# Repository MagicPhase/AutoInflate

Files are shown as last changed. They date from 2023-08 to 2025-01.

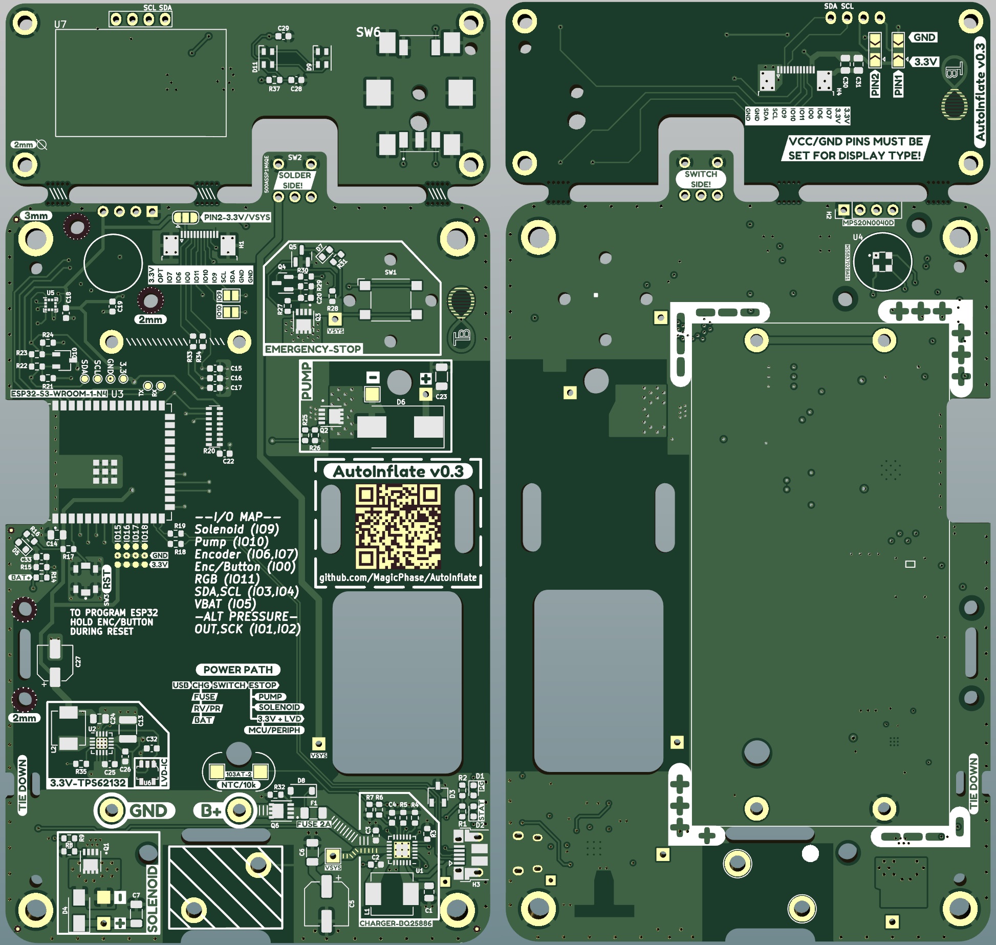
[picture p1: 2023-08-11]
PCB/AutoInflate_V0.3_PCB.jpg

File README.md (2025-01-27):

# AutoInflate
Custom-designed solution for inflation-style sensory and anxiety vests. 

**_In memory of Pedro Martin Colea @tahunus 1/24/24. His initial interest and motivation to create a refined version of my old prototype made this project possible. I'm grateful for the opportunity to have stepped outside my comfort zone and bring this project to fruition. Thank you, Pedro._** 

<br>

###

Welcome! This page contains all the necessary files and instructions to build this device. Please read through each section carefully! If you've found this page, you're seeking to build your own automated inflation device based on this design for inflation-style sensory and anxiety vests. My goal for designing this device was to automate the inflation and deflation cycles on my own [Squease Vest®](https://www.squeasewear.com/). My thanks to [@tahunus ](https://github.com/tahunus) for giving me the inspiration to continue the development of this project!

**_Update 11/28/23: It appears that Squease will be relaunching soon! This is good news for those unable to get a vest prior to the company shutting down operations earlier this year. Yay!_**

It was my intention to design this with a wide range of possible uses while also making it relatively safe given minimal instruction to the user. Here's an overview of some features.
* Handheld/Pocket Sized
* Encoder Style Input
* Emergency Stop Button
* Configurable Pressure Limits
* Adjustable Timed Cycles
* Tap To Activate (coming soon)
* Wireless Function (coming soon)

While this device was created using the Squease Vest, this device could possibly be used with any other inflation-style garment. How this is accomplished will be determined by the end user who will also be responsible for any and all modifications required to mate with this device. 

### ⚠ A note about safety! Under proper working conditions using sanely determined pressure limits and times, this device can operate safely but also has the potential to restrict breathing! This is true for adults, _but especially true for small children._ If you're unsure about how to safely assemble and operate this device, you should consider using the supplied method of inflation for your garment. To make this as safe as possible, I've implemented an E-Stop button on the front side that is a kill switch that removes power from the functional parts. Both the E-Stop and main power switch will effectively render the device unable to retain pressure using the "normally open" air solenoid.

### ⚠ Important note: While the AutoInflate does have safety features like reverse protection and is fused, the charger IC (U1) BQ25886 does not have a 2-cell balance function! This means you should take extra care when choosing and installing the 18650 batteries. Ensure they are both of the same make and model battery. You should also try to match their respective internal resistance to ensure they discharge and recharge evenly, but most importantly to ensure they are at the same level of charge when you install them! If you are unsure about their level of charge, place both cells in an external charger and charge them both together before installation. Once you have two "matched" and charged 18650 batteries then you can safely install them. They will discharge and recharge at the same rate and ensure safe operation by the charger IC.

### It's also important to note that the 18650 holders internally are sized for "flat top" cells and not "button top". The button top cells are too long and will not fit! Please check you're using the correct size 18650 flat-top cells. 

<br>

[STEP 1 - VEST](https://github.com/MagicPhase/AutoInflate#step-1---vest)<br>
[STEP 2 - PLAN](https://github.com/MagicPhase/AutoInflate#step-2---plan)<br>
[STEP 3 - ASSEMBLE](https://github.com/MagicPhase/AutoInflate#step-3---assemble)<br>
* [STEP 3.1 - Main PCB](https://github.com/MagicPhase/AutoInflate#step-31---main-pcb)<br>
* [STEP 3.2 - Display PCB](https://github.com/MagicPhase/AutoInflate#step-32---display-pcb)<br>
* [STEP 3.3 - First Power-Up](https://github.com/MagicPhase/AutoInflate#step-33---first-power-up)<br>
* [STEP 3.4 - Final Assembly](https://github.com/MagicPhase/AutoInflate#step-34---final-assembly)<br>

[STEP 4 - SOFTWARE](https://github.com/MagicPhase/AutoInflate#step-4---software)<br>
* [STEP 4.1 - UI Description](https://github.com/MagicPhase/AutoInflate#step-41---ui-description)<br>
* [STEP 4.2 - Code Explanation](https://github.com/MagicPhase/AutoInflate#step-42---code-explanation)<br>
* [STEP 4.3 - Modify The Menus](https://github.com/MagicPhase/AutoInflate#step-43---modify-the-menus)<br>

## Please read through these hardware sections before considering a BOM.

[3D Printed Parts](https://github.com/MagicPhase/AutoInflate/blob/main/Materials.md#-3d-printed-parts-)<br>
[Pressure Sensor Manifold Options](https://github.com/MagicPhase/AutoInflate/blob/main/Materials.md#-pressure-sensor-manifold-options-)<br>
[Fasterns and Metal Parts](https://github.com/MagicPhase/AutoInflate/blob/main/Materials.md#-fasterns-and-metal-parts-)<br>
[PCB](https://github.com/MagicPhase/AutoInflate/blob/main/Materials.md#pcb)<br>
[Electrical Components](https://github.com/MagicPhase/AutoInflate/blob/main/Materials.md#electrical-components)<br>
[Non-Electrical Components](https://github.com/MagicPhase/AutoInflate/blob/main/Materials.md#non-electrical-components)<br>

[0.3v FIRMWARE](https://github.com/MagicPhase/AutoInflate/blob/main/FIRMWARE/AUTOINFLATE_0.3.1V.ino)<br>

# _**STEP 1 - Vest**_

It's advisable that you gain access or purchase the desired inflation garment first. This will be an important step to understanding the operation of the garment and the possible benefits of using an automated inflation device for such a garment. At the time of this writing, the Squease Vest® has been out of production for most of 2023. However, recent news says they might be starting up again! 

# _**STEP 2 - Plan**_

<br>

Determine what hardware is needed. You'll need to acquire the parts needed to craft your AutoInflate so go over these sections and start building your purchase list. As of this writing, building a single AutoInflate could cost between $200-300 depending on the availability and quantity of parts you buy. One significant cost will be the manufacturing of the unassembled PCB. 

Example: $16 x 5 minimum + shipping to US = $100. [PCBWAY](https://www.pcbway.com/).

* [3D Printed Parts](https://github.com/MagicPhase/AutoInflate/blob/main/Materials.md#-3d-printed-parts-) Go over the necessary 3D printable parts you'll need. You can use a print service such as [Shapeways](https://www.shapeways.com/) or any other printing service that's capable of reproducing the needed resin parts. I've included some helpful notes beside the parts to guide you in your decision-making. DIY printing is an option, of course, however, the enclosure may be tricky to print if you don't have experience with large flat surfaces. I'd recommend a print service for this unless you feel comfortable doing this part. I had many failures until I figured out my printer!<br>

* [Pressure Sensor Manifold Options](https://github.com/MagicPhase/AutoInflate/blob/main/Materials.md#-pressure-sensor-manifold-options-) Determine which pressure mainfoild you wish to use. I recommend using the parts listed for [MS583702BA01](https://www.digikey.com/en/products/detail/te-connectivity-measurement-specialties/MS583702BA01-50/6221400). I've not fully tested the MPS sensor variant! This is important because the two pressure sensor variations require different resin prints as well as sensor hardware. The MS583702BA01 sensor has the benefit of having a higher pressure limit but is also slightly more expensive. _Note: there are I2C pads exposed so a completely different sensor could be used if the internal space allows for it!_
* [Fasterns and Metal Parts](https://github.com/MagicPhase/AutoInflate/blob/main/Materials.md#-fasterns-and-metal-parts-) Make a list of the various fasteners and metal parts needed.
* [Electrical Components](https://github.com/MagicPhase/AutoInflate/blob/main/Materials.md#electrical-components) Make a list of the various electrical parts needed.
* [Non-Electrical Components](https://github.com/MagicPhase/AutoInflate/blob/main/Materials.md#non-electrical-components) And also make a list of the non-electrical parts needed.

And finally, the PCB.
* [PCB](https://github.com/MagicPhase/AutoInflate/blob/main/Materials.md#pcb) I've provided the appropriate Gerber files for a PCB manufacturing service. Both the main and display PCBs are together and separated during assembly. If you plan to DIY, I'd recommend ordering the solder stencil as well!
* Follow the [BOM](https://github.com/MagicPhase/AutoInflate/blob/main/PCB/AutoInflate_V0.3_BOM.html) and build the appropriate list of SMD components. (Save to BOM.html and open in any browser.)

# _**STEP 3 - Assemble**_

Once you have all the parts and pieces, you can move to assembly and testing! 

## _**STEP 3.1 - Main PCB**_

These instructions assume you have moderate to advanced skills necessary to solder the surface mount parts. You can use the included interactive [BOM](https://github.com/MagicPhase/AutoInflate/blob/main/PCB/AutoInflate_V0.3_BOM.html) to guide you as you build the PCB. 

* Please refer to [Materials](https://github.com/MagicPhase/AutoInflate/blob/main/Materials.md) section as you progress!<br>

* The top side of the main PCB should be soldered first. All the surface mount parts are located on one side with one exception being the MS5837 pressure sensor which should be done after soldering all the top side SMD parts. A hot plate can be used for the top side soldering while  **_the back side pressure sensor MS5837 requires a hot air station to attach!_** The alternative MPS sensor requires through-hole soldering. It's important to attach the sensor prior to the completion of the PCB assembly due to its proximity to the battery holder. It's possible to reflow this after, but you'd need to cover or remove the battery holder so as to not damage it from the heat! Ensure all the parts are soldered correctly and remove any solder jumps between pins. **This is especially important for the USB and display ribbon connectors!** 

||||
| :--: | :--: | :--: |

* Attach and solder the remaining components like the battery holder, pump (including shock mount), and solenoid. Also, check that the motor polarity is correct! Depending on the specific model of the solenoid, it may also have a polarity. If the solenoid shows no polarity, connect whichever way is convenient to the pads. Both pump and solenoid wires run from the backside to the front through holes in the PCB.
* The shock mount foam piece should be thin open cell foam about 7cm x 2cm in size and no more than 5mm thick un-compressed. This is important so as to not overfill the cavity surrounding the pump motor. <br>

||| |||
| -- | -- | -- | -- | -- |

* Prepare and attach the MS5873 sensor manifold. Don't forget the O-Ring! Refer to the exposed example of the assembly. Once done you can mark and cut the lengths of silicon tubing to connect the various parts. The larger is 1/8"(3mm) ID x 15mm in length and the smaller is 3/32"(2mm) ID x 9mm in length.<br>

|||
| -- | -- |

* The finished main assembly should now look something like this. Note there is a small slot marked "Tie Down" on the PCB for a single zip tie to attach. Don't over-tighten or you'll cut off the airlines. This is meant simply to contain the tubing. Also, remember that ALL the through-hole parts are on the back side! Make sure the power switch is correctly mounted before attempting to fit into the case! <br>

||||
| -- | -- | -- |

* Before moving on, this is a good time to glue the two light pipes in place as well as the 5 threaded metal inserts. Using CA glue, glue the indicator LED light pipe into the TOP case as well as the E-Stop light pipe. During testing, the E-Stop light pipe is more optional because the LED tends to light up the entire E-Stop button. However, it's important to glue the TOP indicator before assembling further. Also using either CA glue or epoxy, glue the 5 inserts into their respective notches in the BOTTOM case halve.

|||
| -- | -- |

## _**STEP 3.2 - Display PCB**_

The next step is to solder and assemble the display PCB. This is done in two parts.
1. Solder the SMD parts using air hot like capacitors, resistors, ribbon cable socket, and encoder.
2. **The last step is to attach the OLED, but it first needs to be fitted into the casing.**

* Please refer to [Materials](https://github.com/MagicPhase/AutoInflate/blob/main/Materials.md) section as you progress!<br>

* The display board has components on both sides and may be tricky to solder. Because the encoder is a surface mount part, I'd recommend attaching that first because it requires a little extra heat. Once you have the display board soldered MINUS the OLED, connect the solder jumpers on the back side to match your OLED pin configuration. Specifically which pin is power and ground. This should be silk-screened on the device and you should jumper the correct pins to match.<br> <br>

* Start by laying out the TOP case, OLED, and the display PCB. Set the OLED into the case, then arrange the PCB to fit with the screw holes visible. Make sure the pins from the OLED header pass through the appropriate holes. Screw the PCB in place with the M2 self-tapping screws. Make sure everything is secured and finally solder the 4 header pins. This will set the proper distance between the OLED and PCB. Note that the OLED is held in place by the pin header and the allowed seat internal to the case. You can now remove the PCB assembly by pivoting backward at the bottom. This will make it easier to attach the ribbon cable if you don't feel comfortable doing it inside the case.

|| | | |
| -- | -- | -- | -- |

## _**STEP 3.3 - First Power-Up**_

All the components should be assembled for the first power-on test. On the bench, install the 18650 batteries and attach the ribbon cable between the two boards. Note that the device can't be used directly from USB power! The battery charger requires the batteries to be installed to work properly!

* Please refer to [Materials](https://github.com/MagicPhase/AutoInflate/blob/main/Materials.md) section as you progress!<br>

* ## ⚠Important note: While the AutoInflate does have safety features like reverse protection and is fused, the charger IC (U1) BQ25886 does not have a 2-cell balance function! This means you should take extra care when choosing and installing the 18650 batteries. Ensure they are both of the same make and model battery. You should also try to match their respective internal resistance to ensure they discharge and recharge evenly, but most importantly to ensure they are at the same level of charge when you install them! If you are unsure about their level of charge, place both cells in an external charger and charge them both together before installation. Once you have two "matched" and charged 18650 batteries then you can safely install them. They will discharge and recharge at the same rate and ensure safe operation by the charger IC.

* On the first power-on using a bench supply, you should see the green LED next to the ESP32 light up when the voltage reaches 5.8v if you've followed the schematic and used the specified IC for (U6). U6 is the low-cutoff IC and will cut power to the 3.3v supply when a low threshold of 5.8v is reached. Without any programs running, the OLED should remain blank at this point. Install the 2 x 18650s and connect the micro USB to ensure the charger is working. You should see both the STAT and PG LEDs light up. Both of these LEDs are connected to USB 5v and the "Open Drain" pins on the charger IC (U1). The STAT LED will stop once the batteries are fully charged. If no LED activity is visible on the charger, ensure the batteries are installed in the correct orientation and double-check the USB header for solder blobs!<br>

* Check the E-Stop is working correctly. This is important to ensure the safe use of this device. While powered, press the E-Stop button. This will activate the E-Stop circuit and cut power to both the ESP32, solenoid, and pump indicated by the red LED. If this circuit fails to cut power or doesn't function as intended, please review the SMD components and ensure they match the schematic. This trip circuit will remain active until the device is powered off.<br>

https://github.com/MagicPhase/AutoInflate/assets/104283546/334833f4-76d6-4969-865c-a28765c14681

## _**STEP 3.4 - Final Assembly**_

Finally, it's time to assemble the finished unit. It's easier to disconnect the ribbon cable from the main PCB and reattach it just prior to combining the two case halves. The 1/8" thru-bulk fitting should be attached to the bottom case as well as a final short piece of tubing that should be used to connect the sensor manifold to the thru-bulk port. 

* Please refer to [Materials](https://github.com/MagicPhase/AutoInflate/blob/main/Materials.md) section as you progress!<br>

* The thru-bulk fitting should be placed with the nut on the outside. This allows for a bit more room on the inside for the short tube. The main PCB assembly should fit snuggly inside the case bottom. The short tubing piece and be cut to fit once the PCB has been seated. Make sure the PCB fits onto the two indexing pins that are molded into the case model.<br>

|| 
| -- | -- |

* Lay both halves flat on a table and attach the ribbon cable. Each of the sockets has a bottom carriage that needs to be pulled out slightly before inserting the ribbon cable. The cable should be inserted all the way with the shiny metal pins facing up then evenly push the carriage into place. This is easy to mess up and have the cable seat slightly crooked. This needs to be perfectly straight to work correctly.

|| | |
| -- | -- | -- |

* Place the E-Stop button into the guide holes in the PCB. While keeping the BOTTOM case on the table, rotate the TOP half over and allow the ribbon cable to fold over itself. The two halves come together by inserting the single TOP screw mount into the BOTTOM case at an angle. Then pivoting down over the E-Stop button and aligning the remaining screw holes. It's important to remember the forwardmost screw mounts make a near-zero clearance between the PCB and TOP case. Because of this, it's necessary to slightly force the TOP case as it pivots onto the BOTTOM case. As the two halves come together, it's necessary to gently guide the E-Stop button into place under the casing to not be crushed or cause assembly issues. I've included a video showing how to disassemble and reassemble the device at this point. Watch this first! ---> https://www.youtube.com/watch?v=enySG7zAhLk<br>

|| 
| -- | -- |

* Once done, use the remaining 5 screws 4 x (M3-0.5 x 12mm) and 1 x (M3-0.5 x 8mm) to secure the case.


## _**STEP 4 - SOFTWARE**_

Uploading the firmware is done using the [Arduino](https://www.arduino.cc/en/software) IDE or other compatible software to compile and upload the code to the ESP32.

The latest firmware can be found here. --> [FIRMWARE](https://github.com/MagicPhase/AutoInflate/tree/main/FIRMWARE)

A note about programming the ESP32-S3 using the onboard USB to UART.

To program the ESP32 you need to hold down the encoder button and then power on. This shorts PIN 0 to ground putting it into program mode. Then plug in the USB and check for a COM port.

For some reason, the Arduino IDE picks a random hardware ID for the ESP32. It will probably show up as some flavor of S3, which it is, but the compiler profile needs to know that it's an "ESP32S3 Dev Module"! It will probably still compile and upload, but the random ESP32-S3 module profile usually doesn't have the correct settings or correct IO mapping. The latter issue caused me great headaches when I was programming for the first time. This also means when resetting after a flash, the device ID changes and you need to reselect it if you're monitoring for serial connection. All my ESP32s act this way on the newer Arduino IDE so I assume it's not an isolated problem.<br>



Also, if you plan to use serial debug back over the USB, make sure you have the "USB CDC" option enabled on your first flash otherwise no traffic.<br>



## _**STEP 4.1 - UI Description**_

A description of the various menu items.

**_Important note: All entered settings will be valid for the current powered cycle. If you wish the settings to remain during future uses, use the SAVE function on each specific subconfig menu!_**

### Main Page



* Current Pressure - Displays the current pressure of the system in PSI (pound per square inch).

* STOP - This function will stop all current cycles and turn off the pump and solenoid.

* HUG - This function is intended for a one-time inflation cycle. These settings can be changed and saved in the CONFIG menu.

* PROFILE - This function is for multiple cycles within a total cycle duration time. These settings can be changed and saved in the CONFIG menu.

* CONFIG - This accesses the main subconfigure selection menu.

* ACTIVITY - This will animate whenever a cycle is running regardless if there's any current activity from the pump.

* TIME REMAINING - This counter shows the current remaining time until the active cycle stops.

* BATTERY - Shows the remaining battery life. The low mark is referenced to the low voltage cutoff IC voltage (U6).

### Config Page



* A simple menu for the selection of the various subconfiguration menus. At the time of this writing, not all menus are active.

### Hug and Profile



Both the Hug and Profile menus are similar. The Hug settings are intended for one-time inflation cycles while the Profile is meant for multiple cycles based on a total cycle time.<br>

**_Important note: Neither the Hug or Profile cycles will run if the On Time and Cycle Time are zero!_**

* Target Pressure - The desired target pressure to maintain during an on cycle.

* On Time - The amount of time to maintain the target pressure before reverting to a zero pressure state within the cycle time.

* Off Time - The amount of time for the system to remain at zero pressure before re-inflating within the cycle time.

* Cycle Time - The hard time limit for multiple inflation cycles. This time limit will allow for multiple on/off times within this limit, but will not be divided evenly. 
  * Example 1: On Time = 40 seconds, Off Time = 20 seconds, Cycle Time = 5 minutes (5:00). There will be a total of 5 on/off cycles within the 5 minutes.
  * Example 2: On Time = 30 seconds, Off Time = 60 seconds, Cycle Time = 9 minutes and 20 seconds (9:20). There will be a total of 6 on/off cycles with a remaining 20 seconds of on time before the cycle limit is reached and stops the run.

* BACK - Use to navigate back to the subconfig selection menu.

* HELP - An on-screen description of the various items.

* SAVE - This function will save the current entered pressures and times within for future use if powered off.

### AIRSYS



This page is important for proper function! Please adjust these settings based on personal therapeutic choices such as maximum allowed pressures and pump speeds.

* Pump Max - This sets the maximum speed of the pump. For the maximum performance, the highest setting should be used. However, if the audible pump noise is an issue, you can reduce this speed to quiet the pump motor at the expense of a slower inflation time. Consideration should be given because the slower speed may fail to reach a target pressure within a given On Time cycle.
  * Example: If the device is unable to inflate the vest's volume of air at a given "On Time", try increasing the pump speed or increase the On Time to achieve the target pressure within the On Time cycle.
 
* P.Max - This sets the maximum allowed target pressure in both the Hug and Profile menus. (Note: The limit of this adjustment is hard coded.)

* THRESH - This adjusts the threshold limit for the ramping function. This allows for a slow ramping of the pump motor at the top and bottom of the target pressure making for a quieter start and stop. Change to 0 if you don't want this function.

* BACK - Use to navigate back to the subconfig selection menu.

* HELP - An on-screen description of the various items.

* SAVE - This function will save the current entered pressures and times within for future use if powered off.

## _**STEP 4.2 - Code Explanation**_

This section is to provide a brief description of the menu system in code. This may be helpful if you wish to add or modify the menus.

It's important to remember this menu system is based on a one-button interface with the encoder and that all stored and displayed values are derived from the ENCODER INPUT VALUE! This was a design choice based on my limited knowledge of coding in general and my need to keep things relatively easy to adjust with only the encoder as an input device. This meant jumping through some hoops to achieve this. For example, all pressures and stored and computed as (millibar * 100), but the displayed and adjustable values are all in 0.1 PSI increments for ease of use. This means the stored value in (millibar * 100) is computed bidirectionally from the displayed PSI in 0.1 increments from the encoder input and also recalled from memory as (millibar * 0.0146) both computed and displayed as a whole number which is the encoder input value. This gives around 6.8 millibar resolution which is more than enough for this application. Furthermore, variables like the pump PWM are also derived from the encoder input but are further divided by the number of pixels in the graphic representing the pump speed. In this case, the pump speed is mapped to the number of pixels on the display graph which gives 51 levels of adjustment. This mapping can be removed with the pump PWM reflecting the exact encoder input, but the resolution is 10 bit giving 1024 levels. 10 bit was chosen for greater control over low PWM values in the 'airSYSLOOP()' function.

The code keeps track of the current page and element number based on the encoder value and whether the button was pressed on a specific element. The "main" and "sub-config" selection pages have specific/special action functions that are different from the individual sub-config pages which are more generalized. 

Displayed data on the various pages is handled with the 'displayData()' function in 'void loop()' which loads the data to display based on the current page number and results in a continuous page update of that data. Each specific page function contains the relevant data to display such as graphics and variables as well as things like cursor positions and specific variable constrain limits. 

Both the encoder and button are handled with interrupt functions. While the button function is an interrupt, it's also debounced and checked on each loop. A button action happens using a combination of page number, element, and encoder value. This happens when the page number is passed to 'buttonPressFunc(pageNumber)' and is a one-time action that changes the continuously displayed data.

Here are a few flowcharts that describe how data is displayed. Remember both the first two pages, Main and Sub-Config Selection pages have different action functions than the more generalized sub-config pages themselves. Also, it's important to remember these charts are generalized and don't contain the total of executed functions during a button press but can be a useful guide for the order of execution! 

## Main and Config Page Blocks



## Sub-Config Pages (PROFILE, HUG, etc...)



The specific sub-config page elements are selected and changed in real-time based on the element number and whether 'changeValue' is true or not.

## _**STEP 4.3 - Modify The Menus**_

Here's an example of changing and adding elements to the last config page which is currently empty (0.3v). This is the last config page 'configPage8()' (which needs to be added), and the 10th page in the system 'pageNumber = 10'. We will change the onscreen title from "----------" to "TEMP". We will then add a new onscreen variable "TEMP" with a selectable range from 0-255 and include the 'Preferences' entry to store the variable in flash. Also included will be the default onscreen back and save buttons. This will result in 3 total elements for 'configPage8()'. (0, Back) (1, TEMP) (2, SAVE) "Back" and "Save" functions are special cases and handled by the 'subconfigPageActions()' function during a button press. The zeroth element goes back to the sub-config selection menu by default and only needs the onscreen graphical elements in each specific sub-config page. The Save function can be at any element number except zero and also only needs the onscreen graphical elements in each specific sub-config page. See the template below 'configPage8()' for an example of the Save function on element number 2. All other onscreen elements will need specific graphics, text, variable handling, encoder limits, etc...<br>



Nearly all the graphics for this project were generated using [lopaka.app](https://lopaka.app/) U8g2 code generator. This webapp has greatly reduced the time for generating the graphical elements so check it out!



* First, change the displayed title of the 8th config page from "----------" to "TEMP" in the following section of 'void configMainPage()'.<br>

```
else if(encoderInput == 8)//PAGE 8 NA
  {
    u8g2.setDrawColor(1);
    u8g2.setFont(u8g2_font_profont22_tr);
    //u8g2.drawStr(11, 32, "---------"); //<--From this.
    u8g2.drawStr(39, 32, "TEMP");        //<--To this.

    if(!flash)
    {
      u8g2.setDrawColor(1);
      u8g2.drawFrame(89, 54, 10, 10);
    }
    else
    {
      u8g2.drawBox(101, 54, 10, 10);
    }
  }
```

* Second, add a 10th case to the 'displayData()' function below case 7. This will be the looping display data for the 8th config page 'configPage8()' which is 'pageNumber = 10'.<br>

```
void displayData()//CONTINUOUS EXECUTE
{
  switch (pageNumber)
  {
    case 1:
      mainPage(); //MAIN PAGE
      break;
    case 2:
      configMainPage(); //CONFIG PAGE
      break;
    case 3:
      configPage1(); //PROFILE
      break;
    case 4:
      configPage2(); //HUG
      break;
    case 5:
      configPage3(); //AIRSYS
      break;
    case 6:
      configPage4(); //MOTION
      break;
    case 7:
      configPage5(); //CONFIG
      break;
    case 10:
      configPage8(); //<---NEW TEMP PAGE!!
      break;
    default:
      break;
  }
}
```

* Third, add a function 'void configPage8()' with the relevant data.<br>

```
void configPage8()//TEMP
{
  if(SAVE){SAVE = false;} //Important! Because the save function is picked up in the button handle portion instead of on each sub-config menu, this function forces the execution when the encoder input is equal to the element number for the save function only!

  //Initial page graphics.

  u8g2.setDrawColor(1);
  u8g2.drawXBMP( 0, 57, 9, 7, image_Pin_arrow_left_9x7_bits);        //Back button.
  u8g2.drawXBMP( 104, 53, 24, 11, image_KeySaveSelected_24x11_bits); //SAVE button.
  u8g2.setFont(u8g2_font_profont22_tr);
  u8g2.drawStr(19, 35, "TEMP");

  //Using the 'u8g2.drawStr()' may require the use of 'dtostrf()' to disaply data.
  char buf[5];
  int temp = tempVar;
  dtostrf(temp, 3, 0, buf);
  
  u8g2.setFont(u8g2_font_profont22_tr);
  u8g2.drawStr(72, 35, buf);

  //Alter the displayed data or variables based on encoder input and element.
  
  if(!changeValue) //Check if we're changing a selected value.
    {
      if(encoderInput == 0)//BACK
      {
        if(!flash)
          {
            u8g2.setDrawColor(0);
            u8g2.drawBox(0, 57, 9, 7);
          }  
      }
      else if(encoderInput == 1)//New Temp Variable
      {
        encoderInputTemp = tempVar;
        if(!flash)
        {
          u8g2.setDrawColor(1);
          u8g2.drawFrame(70, 19, 38, 18);
        }     
      }
      else if(encoderInput == 2)//SAVE
      {
        if(!flash)
          {
            u8g2.setDrawColor(2);
            u8g2.drawRBox(104, 53, 24, 11, 1);
          }
          SAVE = true;//Set SAVE flag for button press trigger when the save icon is highlighted. (Special case)
      }
    }
    else //Now if changeValue is true, we are making changes to the specific element that was selected. Element == 0 goes back to the sub-config selection menu by default!
    {
      if(element == 1)//TEMP VARIABLE
      {
        encoderConstrainValMin = 0; 
        encoderConstrainValMax = 255;  //It's important to set a maximum encoder input value!
        tempVar = encoderInput;        //Live update to variable.
      }
      else if(element == 2)//SAVE
      {
         //LEAVE BLANK. The save function is checked by setting 'SAVE = true' above and picked up in the 'subconfigPageActions()' function.
      }
    }
}
```

* Fourth, add the temp global variable near the top of the code.<br>

```
byte tempVar = 0;
```

* Fifth, add the number of elements of the new temp page to constrain the encoder behavior. We are adding only two elements to this page so we change the 11th position of 'PageElements[11]' from 0 to 2. The zeroth element is a back function by default in the sub-config menus. The page order is as follows: BLANK, MainPage, ConfigPage, Profile, Hug, AirSYS, Motion, Config, WIFI, -----, (NEW TEMP PAGE).<br>

```
int PageElements[11] = {0, 3, 8, 6, 4, 5, 0, 3, 0, 0, 2};
```

* Sixth, add the correct 'Preferences' entry to the 'storedData()' function to store in flash. In the 'storedData()' function, change the case 10 (page number 10) execution to this...<br>

```
case 10:
 if(!RW) //READ
 {
  tempVar = preferences.getUInt("temp_Var", 0); //Check if tempVar is present, if not set default value '0'.
 }
 else //WRITE
 {
  preferences.putUInt("temp_Var", tempVar); //Write tempVar to flash at 'temp_Var' namespace in Preferences ESP32 storage function.
 }
 break;
```

* Seventh, add a function to pull stored value from flash on power up in 'void setup()'.<br>

```
storedData(10, 0); //Page number 10, '0' for read.
```

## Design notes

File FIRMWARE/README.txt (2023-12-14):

AUTOINFLATE V0.3.1 - 11/18/23
BY Tevian Busselle 

This version (0.3.1v) only has the MS5837 pressure sensor enabled, and will not work with the MPS sensor yet. This also requires the MS5837 library found here. https://github.com/bluerobotics/BlueRobotics_MS5837_Library Copyright (c) 2015 BlueRobotics

This ino file must be compiled and uploaded using the Arduino IDE with all relevant ESP32 libraries.

What works:
All basic functions like timed inflation cycles work. This includes a one-time cycle "HUG" and a repeating timed cycle "PROFILE". 
The ability to configure basic settings such as pressure settings, pump speeds, and times. Each menu also has a save function for continuing use after power cycles. 

What's doesn't work:
The tap to activate with the onboard IMU has not been coded for yet. This also includes any WIFI/Bluetooth options. Both of these menus are empty at the moment.

Important interface notes:
* Inputting pressures over the selected maximum will reduce the value to the maximum. 
* An inflation task "hug or profile" will only execute if the times are not zero!
* The values under all menus except CONFIG are usable for the current power cycle. The SAVE function will store the values for future use. 
* Changing the CONFIG menu items requires a reset to take effect. This is forced in the CONFIG navigation.

Operation notes:
* The pump's noise level can be tuned by changing the maximum PWM in the AIRSYS menu. The threshold ramping value can also be adjusted to allow for a softer start/stop
  that can make the pump quieter during the initial start and topping maintenance.
* Motor pulses for system feedback. (One) pulse for system functions such as the save function or failure to set a variable. (Two) pulses single the end of an inflation task.
* the threshold ramping pressure works by ramping the pump speed from a low minimum to a high speed across a small pressure window at the beginning and end of an inflation cycle.
  This means the pump speed will remain low until the pressure sensor sees an increase in pressure. Depending on the volume of air required to inflate the vest or vessel,
  this can result in an extended duration of low pump output at the beginning of the inflation cycle. If this happens, try decreasing the threshold amount, increasing the pump speed,
  ensuring the total volume of air in the vest or vessel is reduced (adjusting the fit), or setting the threshold number to 0 which disables this feature.
  
---------------------------------------
Choosing the correct pressure is important! Correct pressure is a matter of personal choice 
based on your therapeutic needs. While I can't give a specific pressure and time duration, 
I can give a few useful guides. Don't forget to 'SAVE' the settings if you find something you like for future use!

Example Hug setting: 
This will provide a rather quick and sudden sense of pressure on the torso for 30 seconds or more if needed. 
Adjust the pressure as needed!

  Hug Menu
    Pressure: 1.0-1.5
    Time: 0:30-1:00
  CONFIG Menu
    Pump PWM: 100%
    T.MAX: 0.0-0.2  

Example Profile setting: 
These settings will give a gentle continuous rise and fall of pressure. 
This can be very relaxing or decompress from anxiety or stress.

  Profile Menu
    Pressure: 1.0
    On-Time: 0:45-1:00
    Off-Time: 1:00-2:00
    Cycle Time: 10:00-15:00
  CONFIG Menu
    Pump PWM: 60-75% (This will make the pump quieter) 
    T.MAX: 0.3-0.4 (This will result in a softer start/stop)

Notes about the code:

All variables including pressures, settings, and times are converted from the (encoderInput) counter. This has the effect of limiting the divisions of certain
variables like pressure and pump speeds. For instance, while the pump PWM has a value from 0-1023, this would require the encoder to be turned too many times
to achieve the maximum value. The division of the PWM speed is dictated by the number of pixels in the display graph. This is handled via the map function to
convert 0-1023 steps into 51 pixel steps. The raw PWM number is stored for use while the displayed value/graph is converted from that stored number. 

While the displayed pressures are in PSI, the stored pressure values are in (mBar * 100). Example: The default stored value for the maximum "selectable" 
pressure from the interface is (13788 / 100 = 2PSI) and is stored in (airSys.maxPressure). 

When uploading the firmware it's important to remember there is a hard-coded maximum system pressure. In the code, this variable sets the maximum encoder input 
value allowed when adjusting the maximum pressure in the AIRSYS menu. This variable is called (MaxPressure). 
Example: MaxPressure = 41 is 4.1PSI (encoderInput / 10). If the "selectable" pressure is also 4.1PSI then the stored value in (airSys.maxPressure) would be 27576. 

When the selectable pressure is reduced, all stored pressures in the different run scenarios are also reduced to match this. So, while the P.MAX adjustment in the 
AIRSYS menu sets the maximum user-selectable pressure for the different run scenarios, the hard-coded variable (MaxPressure) sets that maximum value for the adjustable 
P.MAX value in the interface.

Default system variables like pressures and PWM are stored in "storedData" function with the relevant variables. The preference function initiates these defaults.

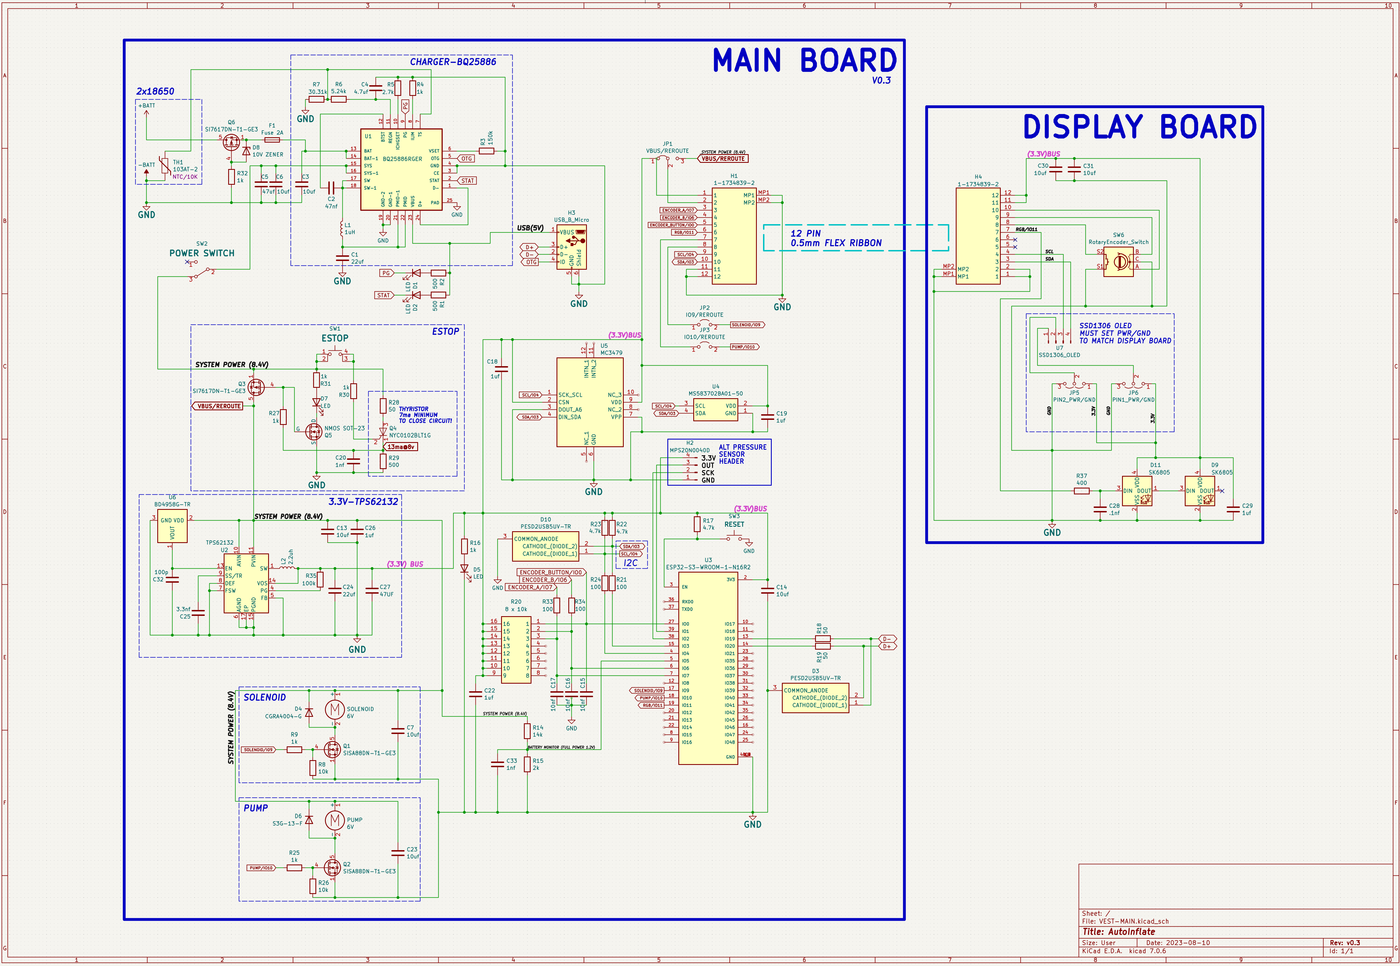
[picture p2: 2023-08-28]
PCB/AutoInflate_V0.3_Shematic.png

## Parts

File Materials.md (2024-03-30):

# Enclosure Hardware

## -3D Printed Parts-

This section outlines the necessary 3D-printed pieces to make and assemble a completed unit. Before printing these parts at home or purchasing from a printing service it's important to note that some parts require specific resin types to ensure proper function.

| Part             | 3D model       | Description/Note  |
| :---             | :---:          | :---             |
| **Top Enclosure**    | TOP_small | Due to the complexity it's recommended this part be made of resin vs filament. To ensure this part is impact-resistant I recommend [Siraya Tech Fast ABS-Like](https://siraya.tech/products/fast-abs-like) or equivalent. Other resins can be used, but beware of the brittleness and impact resistance of the resin. [OBJ](https://github.com/MagicPhase/AutoInflate/blob/main/3D%20FILES/OBJ/TOP.obj), [STL](https://github.com/MagicPhase/AutoInflate/blob/main/3D%20FILES/STL/TOP.stl)|
| **Bottom Enclosure**| BOTTOM_Small | This piece is less complex than the top and could possibly be printed in PLA, PETG, or TPU filament. Print orientation may be critical however to ensure the PCB mounting points and index pins are correctly positioned and flat. For the best results, I recommend this part also be resin printed in [Siraya Tech Fast ABS-Like](https://siraya.tech/products/fast-abs-like) or equivalent impact-resistant resin. [OBJ](https://github.com/MagicPhase/AutoInflate/blob/main/3D%20FILES/OBJ/BOTTOM.obj), [STL](https://github.com/MagicPhase/AutoInflate/blob/main/3D%20FILES/STL/BOTTOM.stl)|
| **Pump Shock Mount** | MOTOR_MOUNT_Small | Shock mount for the pump motor. This piece is ***optional*** to dampen the pump noise during operation, but it's highly recommended! While it's possible to simply zip-tie the pump to the PCB with some foam padding, during operation, this can transfer a large amount of noise and vibration to the unit. There is an option to reduce pump output to limit the noise level, but this shock mount reduced the overall noise by more than half. The walls of the band are <0.8mm for reference. It's possible to have this part filament-printed with PETG or TPU on the vertical axis, but it's also recommended to have this resin printed with [Siraya Tech Fast ABS-Like](https://siraya.tech/products/fast-abs-like), [Siraya Tech Tenacious -Flexible](https://siraya.tech/products/tenacious-resin-flexible-resin), or equivalent flexible resin. This part can be delicate to handle due to the thinnest part being <0.8mm. [OBJ](https://github.com/MagicPhase/AutoInflate/blob/main/3D%20FILES/OBJ/MOTOR%20MOUNT.obj), [STL](https://github.com/MagicPhase/AutoInflate/blob/main/3D%20FILES/STL/MOTOR%20MOUNT.stl)|
| **EStop Button** | ESTOP_Small | This is the EStop button that rests on the EStop switch on the PCB. It protrudes through the PCB with 4 guide pins. These pins are <2mm in diamater. This part could possibly be filament printed, ***however***, due to filament prints having ridges, this might make the guide pins rub and stick to the PCB and interfere with the button press. Because of this, it's recommended this part be printed in a non-brittle red-colored resin. [OBJ](https://github.com/MagicPhase/AutoInflate/blob/main/3D%20FILES/OBJ/BUTTON.obj), [STL](https://github.com/MagicPhase/AutoInflate/blob/main/3D%20FILES/STL/BUTTON.stl)|
| **EStop Light Pipe** *Optional*| EStop_Light_Pipe_Small | This light pipe is an optional part that transfers the red EStop light from the PCB to the top of the enclosure. During testing, however, the light also illuminates the EStop button itself and may not be required. Because of its size, this needs to be resin printed in any clear or white resin. [OBJ](https://github.com/MagicPhase/AutoInflate/blob/main/3D%20FILES/OBJ/ESTOP%20LightPipe.obj), [STL](https://github.com/MagicPhase/AutoInflate/blob/main/3D%20FILES/STL/ESTOP%20LightPipe.stl)|
| **Indicator Light Pipe** | INDICATOR_LIGHT_PIPE_Small | This part is cosmetic and transfers the light from the two RGB LEDs on the top part of the enclosure. This can be printed in resin and possibly filament in either clear or white. [OBJ](https://github.com/MagicPhase/AutoInflate/blob/main/3D%20FILES/OBJ/LIGHT%20PIPE.obj), [STL](https://github.com/MagicPhase/AutoInflate/blob/main/3D%20FILES/STL/LIGHT%20PIPE.stl)|

<br>
<br>

## -Pressure Sensor Manifold Options-

One of the two options ***must*** be decided before finishing a BOM list.

| Part             | 3D model       | Unit Example | Description/Note  |
| :---             | :---:          | :---:        | :---              |
|*Option 1*| ---------- | ---------- | ---------- |
| **Manifold Cap** |MANIFOLD_V0 4_Small|MANIFOLD_V0 4_ASSEMBLE_Small|This manifold is required for the [MS583702BA01](https://www.digikey.com/en/products/detail/te-connectivity-measurement-specialties/MS583702BA01-50/6221400) sensor. It's intended to cover the SMD sensor itself and sealed to the PCB with an O-Ring and M2 screws and nuts. It connects the pump, solenoid, and port, and requires a quality resin print to ensure an air-tight seal around the O-Ring and PCB. I recommend [Siraya Tech Fast ABS-Like](https://siraya.tech/products/fast-abs-like) or equivalent. Current version is V0.5. [OBJ](https://github.com/MagicPhase/AutoInflate/blob/main/3D%20FILES/OBJ/Air%20Manifold%20V0.5.obj), [STL](https://github.com/MagicPhase/AutoInflate/blob/main/3D%20FILES/STL/Air%20Manifold%20V0.5.stl)|
| M2-0.4 x 12mm (2) | M2-0 4 12mm | | Two 12mm screws. |
| M2 nut (2)        | M2 nut | | Two M2 nuts.|
| O-ring (1)  | O-Ring | | One O-ring to seal against the PCB. This part needs to be 9mm(OD) x 5mm(ID) x 2mm. Note that 4.8mm(ID) O-rings will also work.|
|*Option 2*| ---------- | ---------- | ---------- |
| **Manifold 4-Way** | MANIFOLD_4_WAY_Small | MANIFOLD_4_WAY_ASSEMBLE_Small | This manifold is required for the MPS20N0040D/HX710B pressure sensor assembly. This is a cheaper alternative and can be found on Amazon for a few dollars. This manifold is a 4-way that connects the pump, solenoid, sensor, and port and requires a quality resin print is ensure an air-tight seal around the ports. I recommened [Siraya Tech Fast ABS-Like](https://siraya.tech/products/fast-abs-like) or equivalent.  It is secured with M2 screws. Current version is V0.2. [OBJ](https://github.com/MagicPhase/AutoInflate/blob/main/3D%20FILES/OBJ/Air%20Manifold%20V0.2.obj), [STL](https://github.com/MagicPhase/AutoInflate/blob/main/3D%20FILES/STL/Air%20Manifold%20V0.2.stl) |
| M2-0.4 x 4mm (2) | M2-0 4 4mm | | Two screws are needed to secure the manifold to the PCB.|

<br>
<br>

## -Fasterns and Metal Parts-
List of fasting hardware required for the enclosure and manifold options.

| Part             | PICTURE       | Unit Example  |Description/Note   |
| :---             | :---:          | :---:        | :---              |
| M3-0.5 x 8mm (1)   | M3-0 5 8mm |M3_SCREW | One 8mm screw is required on the back side of the enclosure. |
| M3-0.5 x 12mm (4) | M3-0 5 12mm |M3_SCREW_1 | Four 12mm screws are required on the front side of the enclosure. |
| M2 x 6mm (4) Self-tapping | M2x6 | Display Back | Mounting screws for display PCB.|
| M2 x 6mm (4) Self-tapping | M2x6 |MOTOR_MOUNT_Example | Mounting screws for the motor mount. |
| M2 washers (4) | M2 washer|MOTOR_MOUNT_Example | Washers for the motor mount. |
| M3 x 3 x 5mm (5) Heat Set Inserts | INSERTS | INSERT_example | The bottom enclosure is notched for standard M3 x 3mm thick x 5mm round heat set inserts for 3D printing. The resin doesn't work well with heat inserts so I notched the mounting points so they can be secured with epoxy or SA glue. | 
| 2mm x 22mm (2) Stainless Steal Pins |  pin |pin | Two stainless steel strap pins for the top enclosure. These are optional in case you want to use 15mm straps. The pins should be between 22-25mm in length. [Amazon](https://www.amazon.com/dp/B07M63LPFD?ref=ppx_yo2ov_dt_b_product_details&th=1)|

<br>
<br>

# PCB
Main and Display PCBs. Follow the included link for all current PCB files. [PCB FILES](https://github.com/MagicPhase/AutoInflate/tree/main/PCB)
| Part             | 3D model       | Description/Note  |
| :---             | :---:          | :---             |
| **PCB** | PCB_Small | The provided gerber files contain both the MAIN and DISPLAY PCBs. This PCB is made as one piece and separated during assembly. Current version is V0.3. [PCB FILES](https://github.com/MagicPhase/AutoInflate/tree/main/PCB), [Schematic](https://github.com/MagicPhase/AutoInflate/blob/main/PCB/AutoInflate_V0.3_Shematic.png)|

<br>
<br>

# Electrical Components 
Internal Electrical components.
| Part             | 3D model       | Description/Note  |
| :---             | :---:          | :---             |
| Air Pump|  | Commonly called a "370 Pump" or "Mitsumi R-14 A213" is a 6V rated micro air pump. <br> Picture is from an eBay listing. [eBay](https://www.ebay.com/itm/191898244021) |
| Solenoid Valve Normally Open<br>PND-05A-06 or equivilent |  | Common 5-6V rated N/O solenoid valve. It's very important to use an N/O (Normally Open) valve to ensure safe operation. There are mounting holes on the PCB for a genuine PND-05A-06, but an equivalent can be used with zip-ties. This part should measure approximately 20mm x 15mm x 13mm and have a port with 3-4mm(OD). Sub-miniature 3V valves are NOT suitable! Picture is from an eBay listing. [eBay](https://www.ebay.com/itm/262483459557) Also listed as TDS-V05B 6V.|
| SSD1306 OLED 128 x 64|  | Common 0.96" SSD1306 OLED screen. The Display PCB can be configured for either V/G/SCL/SDA or G/V/SCL/SDA depending on which model you get. Picture from [electronicwings.com](https://www.electronicwings.com/sensors-modules/ssd1306-oled-display). |
| 12pin 0.5mm x 100mm flex ribbon cable | Flex Ribbon | Standard 12pin 0.5mm pitch x 100mm length flex ribbon cable. These are common and can be ordered from Amazon as a "Cable Replacement for PS4" or other controllers. This cable is the link between the main and display PCBs. Picture from [Amazon](https://www.amazon.com/gp/product/B08MVZW6QC/ref=ppx_yo_dt_b_search_asin_title?ie=UTF8&psc=1).|
| 18650 (2) flat-top and<br> 2 cell PCB mount holder|BATTERY|Two standard 18650 flat-top batteries and a 2 cell PCB mount battery holder. Avoid using button top cells! [Amazon](https://www.amazon.com/Battery-Storage-Plastic-Parallel-Projects/dp/B0B1JJZ363/ref=sr_1_3?crid=3AY9UWBKUSLFS&keywords=18650%2B2%2Bcell%2Bholder&qid=1693306644&sprefix=18650%2B2%2Bcell%2Bholde%2Caps%2C145&sr=8-3&th=1) |

<br>
<br>

# Non-Electrical Components 
Internal and external components.
| Part             | 3D model       | Description/Note  |
| :---             | :---:          | :---             |
| Encoder Knob |  Knob | Standard 1/4"(6mm) shaft knob. The knobs I chose are 17mm(d) x 16mm(h) knurled aluminum. The enclosure space allows for approximately 17mm in diameter. These are the specific ones I used. [Amazon](https://www.amazon.com/dp/B07TXYBB7Z?psc=1&ref=ppx_yo2ov_dt_b_product_details) |
|Silicon Tubing| Tubing| *Two different sizes are needed.* For the best fit on the pump and port air lines, use 1/8"(3mm)ID tubing. 1/4"(6mm)OD is recommended but thinner can be used if you take precautions to not kink the lines around corners. For the solenoid valve, a smaller tubing of 2mm(ID) x 4mm(OD) fits best. You should be using two different sizes of tubing and both manifolds are sized to fit this arrangement. Picture from [Amazon](https://www.amazon.com/gp/product/B07V5T31MF/ref=ppx_yo_dt_b_search_asin_title?ie=UTF8&th=1)|
| Low Density Foam | FOAM | Thin low density foam for the motor mount. Any thin compressible foam can be used that's less than 1/16"(1.5mm) when compressed. The noise dampening from the motor shock mount is inversely affected by using too much or too thick of foam. The motor should float in the mount to get the best results. Avoid using high-density foam or neoprene! <br><br> The amount needed is approximately 3/4"(15mm) x 3"(75mm). Picture from [Amazon](https://www.amazon.com/Frost-King-Conditioner-Filters-Open/dp/B000BO68BU/ref=sr_1_3?crid=ZTJQQDA5XK5J&keywords=thin+air+filter+foam&qid=1693389469&sprefix=thin+air+filter+foam%2Caps%2C145&sr=8-3)|
| Thru-Bulk Barbed Fitting | Thru-Bulk | A thru-bulk fitting is used to attach to the outside. The specific size I used was 3/16". I wouldn't use anything bigger as it won't fit the tubing inside. Picture from [Amazon](https://www.amazon.com/gp/product/B08SCDC28R/ref=ppx_yo_dt_b_search_asin_title?ie=UTF8&th=1). |

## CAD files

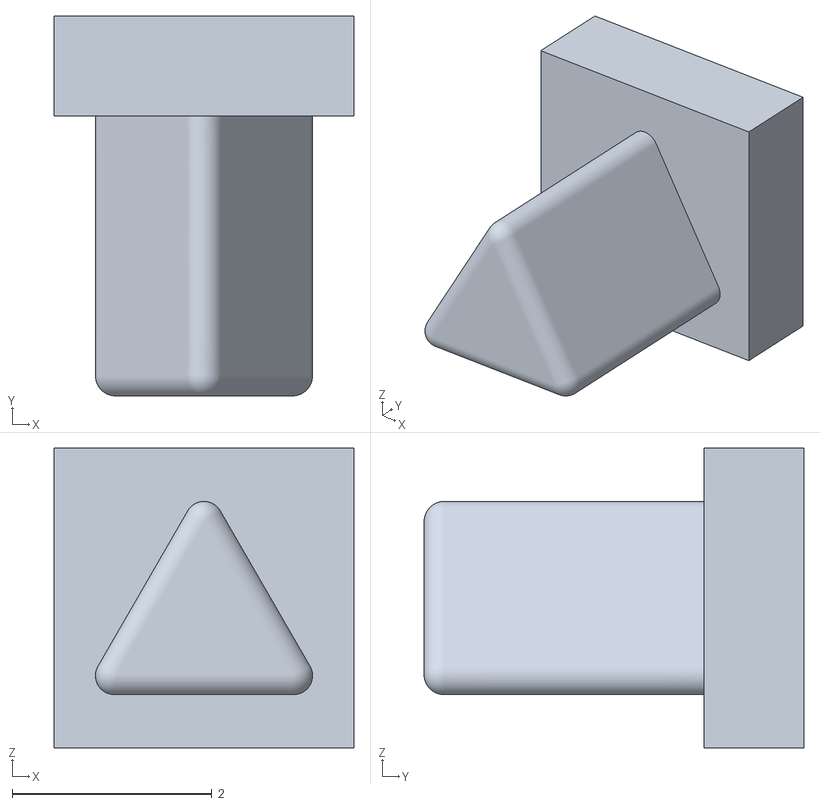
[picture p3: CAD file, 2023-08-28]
3D FILES/STL/ESTOP LightPipe.stl
3.00 x 3.80 x 3.00

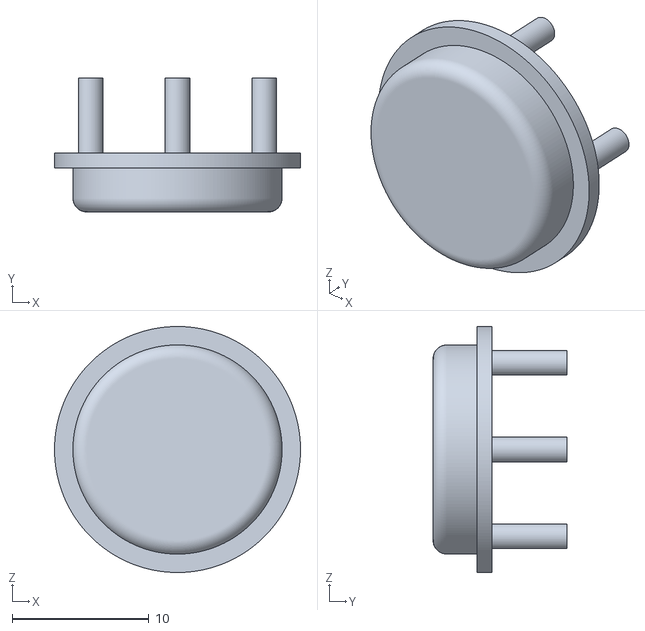
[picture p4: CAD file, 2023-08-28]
3D FILES/STL/BUTTON.stl
18.0 x 9.80 x 18.0

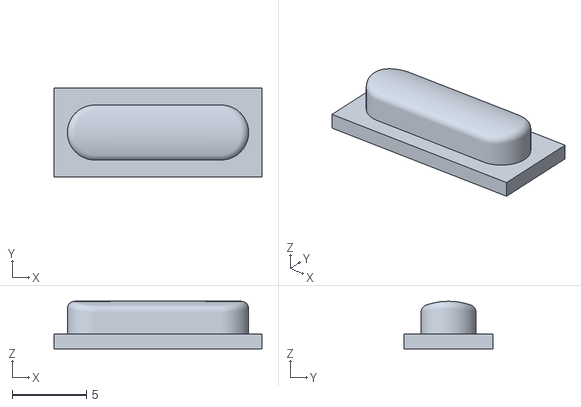
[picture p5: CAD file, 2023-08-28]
3D FILES/STL/LIGHT PIPE.stl
14.0 x 6.00 x 3.20
